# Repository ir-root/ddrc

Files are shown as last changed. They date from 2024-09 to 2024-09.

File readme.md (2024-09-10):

## Welcome to the DDrC Repository!

We published a preprint of the DDrC, this scientific paper can be found here: https://www.biorxiv.org/content/10.1101/2024.02.16.580252v1

The files and instructions for building your own Dynamic Dark Root Chamber for root phenotyping with an infrared camera are available in this repository:
- The build_instructions.pdf contains a detailed building instruction for the chamber
- rootbox.py is the main script controlling the imagetaking
- The '3D print' folder contains all the .stl files for 3D printing the parts (LED_diffusor.stl has to be printed with transparent filament!)
- A disk image file of Raspberry Pi OS with all the necessary configurations made for running the DDrC can be downloaded here: https://drive.boku.ac.at/d/6b6a2837e5644a758b48/

### License
This project contains a 3D model originally designed by ywabiko from printables.com, licensed under CC BY 4.0.
[CC BY 4.0 License](https://creativecommons.org/licenses/by/4.0/)

This project contains a modified version of the 3D model originally designed by DocWeebl from printables.com, licensed under CC BY 4.0.
[CC BY 4.0 License](https://creativecommons.org/licenses/by/4.0/)

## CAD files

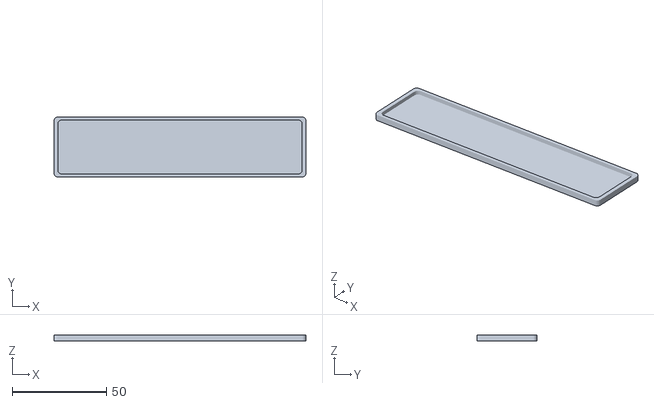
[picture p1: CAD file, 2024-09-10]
3D print/tray.stl
134.0 x 32.0 x 3.00

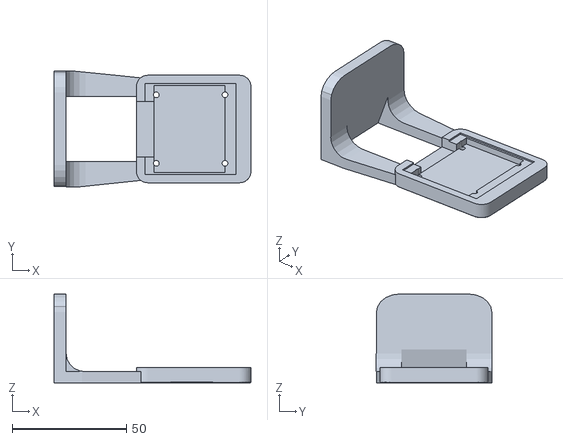
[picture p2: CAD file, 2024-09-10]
3D print/camera_mount.stl
86.3 x 50.7 x 38.8

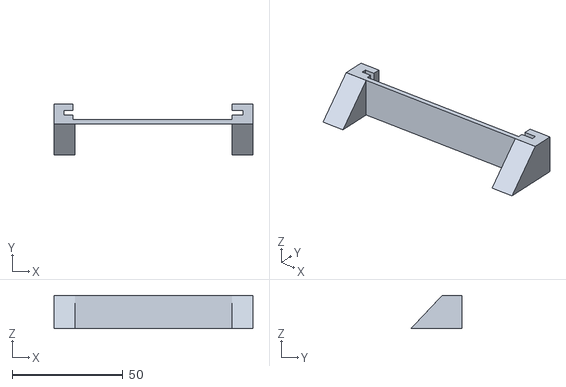
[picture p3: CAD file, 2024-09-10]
3D print/LED_mount.stl
90.0 x 23.2 x 15.0

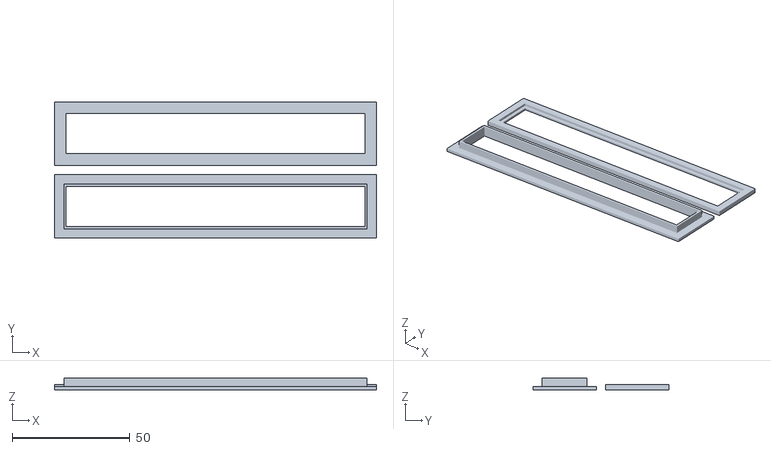
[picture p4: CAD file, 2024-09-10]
3D print/petri_dish_holder.stl
137.0 x 58.0 x 5.00

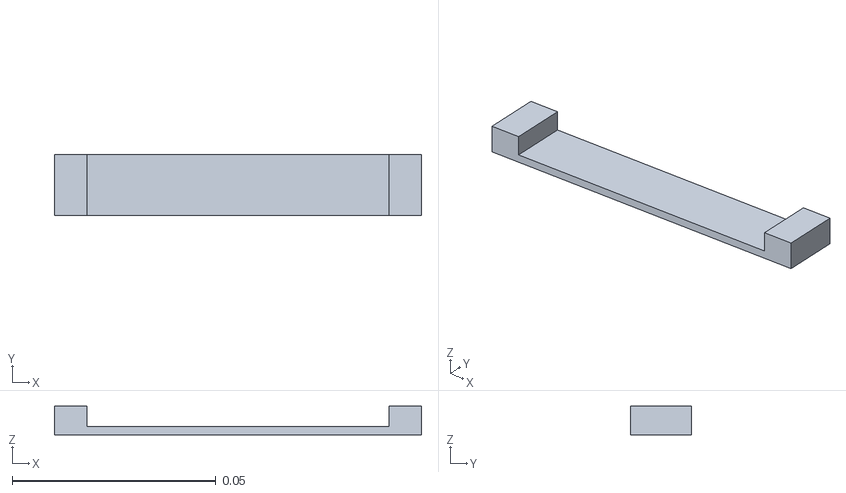
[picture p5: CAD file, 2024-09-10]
3D print/LED_diffusor.stl
0.09 x 0.015 x 0.007

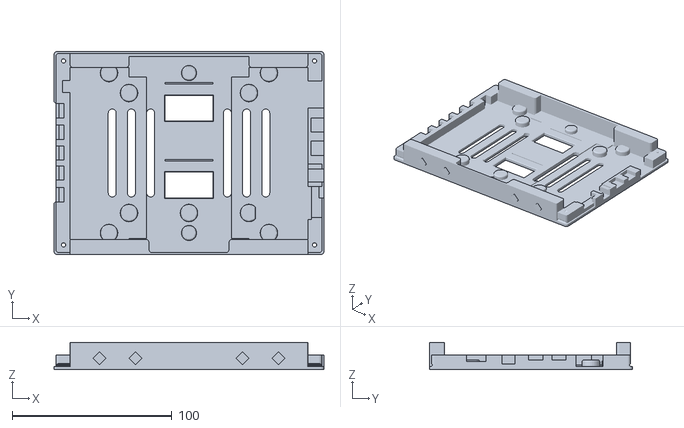
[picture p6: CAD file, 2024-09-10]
3D print/HDMI7_Bottom_v96.stl
168.8 x 127.0 x 17.0

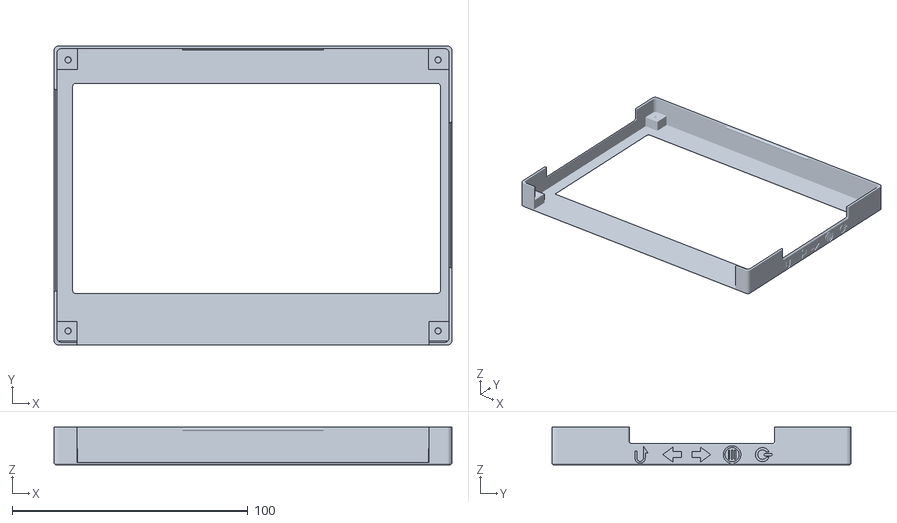
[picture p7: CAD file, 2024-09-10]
3D print/HDMI7_Lid_v44.stl
168.8 x 127.0 x 16.0

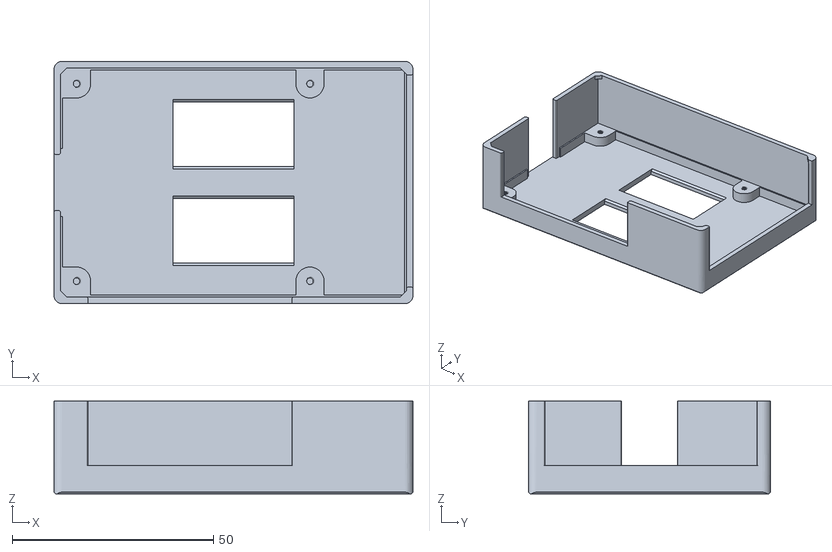
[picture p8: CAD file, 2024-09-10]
3D print/Pi3B_LCD1_v25.stl
89.2 x 60.2 x 23.0

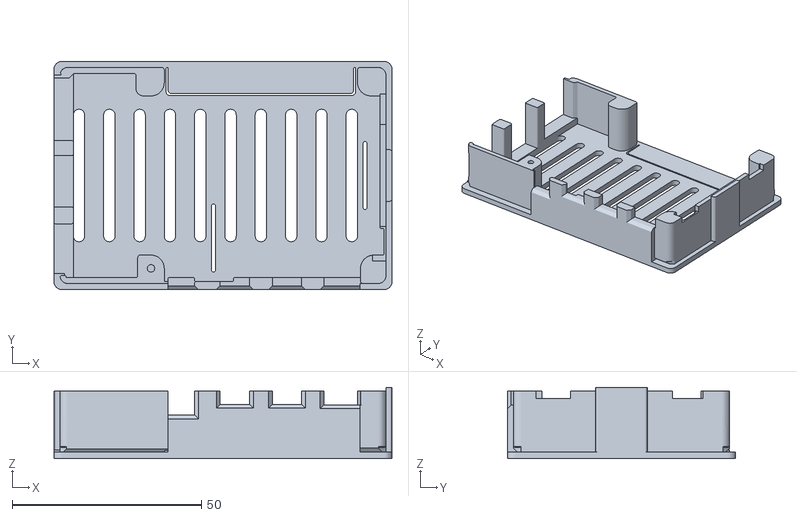
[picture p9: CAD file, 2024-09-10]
3D print/Pi4B_Lid_v22.stl
89.2 x 60.2 x 18.8

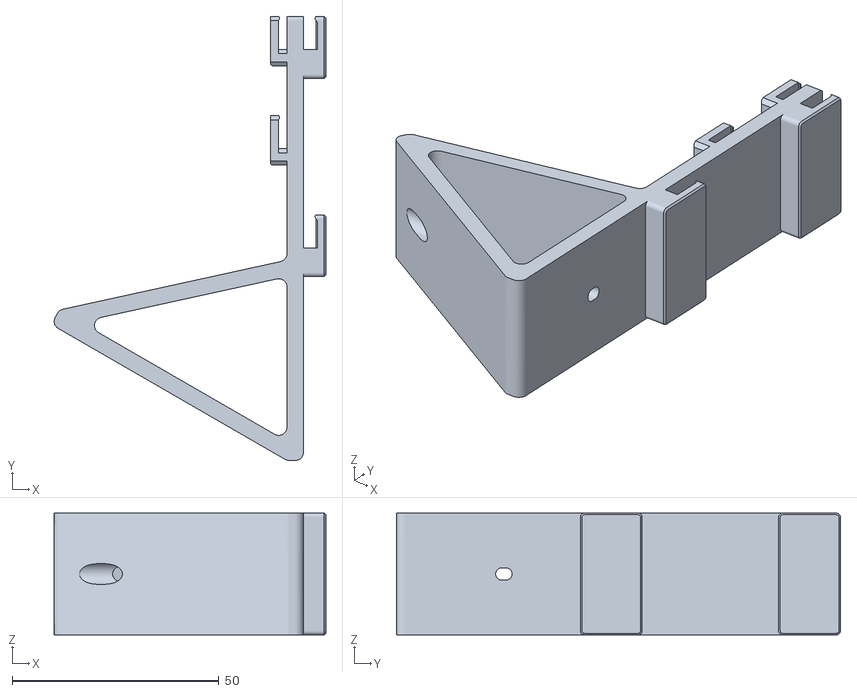
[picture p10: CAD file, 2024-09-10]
3D print/HDMI7andPi_DualHook60_v9.stl
65.8 x 107.5 x 29.5

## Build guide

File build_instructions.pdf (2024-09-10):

### Draft – A more detailed instruction manual with photos will be added later

Parts List:

- Cardboard box (approx 30 x 24 x 9.5 cm)
- Raspberry Pi 4 (1 GB RAM or more)
- Raspberry Pi Camera 3 NoIR (76°)
- Waveshare 7 inch Display Capacitive Touchscreen HDMI LCD (H)
- Raspberry Pi USB-C power supply (5.1V / 3.0A)
- Case for Display and Raspberry Pi
- microSD card
- USB stick
- Iduino ST1168 transistor module
- 12x Kingbright Infrared LED 880 nm L-7104SF4BT
- 2x 13 Ohm resistors
- Strip board (10 cm)
- 6x Dupont connector cables
- 3D printed case and mounts

Tools

- Cutting tools (scissors, knife)
- Ruler
- Small slotted screwdriver
- Soldering iron + solder
- Glue

### 1. Chamber Construction

1.1 Material Selection:
1.1.1 Choose a sturdy, light-blocking cardboard box. The dimensions of the box we used were 30 x 24 x 9.5 cm, so a box of a similar size should be for optimal seedling growth and camera placement.
1.1.2 Optional: Consider using black foam board or paint for improved insulation and to minimize light reflections.

### 1.2 Chamber Assembly:

1.1.2 Cut a slit with a length of 20 mm in one side of the box as a pass-through for the cable connecting the camera module and the Raspberri Pi single board computer.
1.2.2 Cut an opening of 130mm x 20mm in the lid to allow rhizobox insertion. The opening should be at around 220 mm distance of the side of the box.

2. 3D Printing of mounting parts
Download the 3D model files which include:
- case for Raspberry Pi and the 7 inch Display
- camera mount
- carLED mount
- reinforcement for lid slit
- water tray

Use a 3D printer to print those files. PLA and standard printing settings should be fine. For improved sturdiness it is recommended to print the display stand with a higher infill, also PETG will improve strength for this part.

### 3. Camera and Specimen Placement

3.1 Camera Mounting:
3.1.1 Glue the camera mount into the box. Maintain a distance of approximately 20 cm between the camera lens and the rhizobox to capture the entire root growth area. This has already been considered in step 1.2.2.
3.1.2 Rhizobox Preparation:
Design the rhizobox to fit within the chamber. We use square Petri plates with dimensions of 120 x 120 x 17 mm. To create an opening for the shoots to grow we remove the plastic on the lid on one side. Fill the rhizobox with moistened soil and plant the seeds as required on the top of the soil. If necessary use tape on the side of the Petri plates to secure them

### 4. Electronics Setup

### 4.1 Computer Module Configuration

4.1.1 Install Raspberry Pi OS (64-bit with desktop) on a microSD card for touchscreen compatibility and user-friendly interface.
4.1.2 Secure the Raspberry Pi and the monitor into the 3D- printed case
4.1.3 Connect the camera cable to the camera module and the Raspberry Pi
4.1.4 Connect the Raspberry Pi to the monitor using the USB and HDMI cables. Also connect the Raspeberry Pi to the power supply

### 5. LED Lighting System

5.1 LED Placement:

5.1.1 Solder 6 LEDs and the resistor onto a perforated grid plate of 8 x 1.5 cm
5.1.2 Glue the LED mounts into the box. They should be in a distance of around 10 cm from the rhizobox, positioned at a 45-degree angle towards the rhizobox to ensure even illumination. Maintain a distance of approximately 10 cm between the LEDs and the rhizobox to avoid excessive light intensity and reflections.
5.2 LED Circuitry:
5.2.1 Connect the LEDs in parallel using a 13 Ohm resistor to limit current flow and prevent overheating.
5.2.2 Utilize a transistor module to control the LED power supply based on the Raspberry Pi's GPIO signals. This is necessary as the GPIO pins are not designed for a high power output and thus the Rasperry Pi could be damaged if attempting to power the LEDs directly.
5.2.3 Connect the transistor module to the 5V power output of the Raspberry Pi
